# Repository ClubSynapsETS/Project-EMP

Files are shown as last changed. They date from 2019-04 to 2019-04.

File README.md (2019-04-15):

# Project REACH

In the last decade, advences in the domain of electromyography has made it more available to the general public. Which lead to innovation such as a the MYO armband, a commercialised SEMG device. 
These new methods have provoqued a renewed interest in developing more complex prosthetic hands now that more reliable control method to easily control them. Combined with the current trend in biotechnology to solve every problem with machine learning, and you optain the insparation behind project REACH.  

REACH Extends Arm Control for Humans is Myo controlled prothestic arm designed for transradial amputes. It uses a real-time classifier to distinguish between mutually exclusive poses made by human arm by monitoring surface myoelectric (SEMG) generated by muscle contraction on 8 points around the arm. This give us access to 9 distinct commands to control hand with 5 degres of freedom.

## Road Map
### 1) Mechanics
- `/mechanics`        --Contains CAD files and assembling instructions
### 2) Prosthetic Firmware
- `/Firmware`
   - `/Motion_control`     -- Actuator control scheme and modeling of finger mouvement
       - `finger_interce.c`  
       - `finger_interce.h`   
   - `/Pose_classification` --Classifier logic 
       - `pipeline.c`
       - `pipeline.h`
   - `/bluetooth`        -- Bluetooth service connecting to the MYO armband
      - `ble_app.c`
      - `ble_app.h`
      - `myohw.h`             -- Thalmic lab's BLE command and configuration list
   - `/main`             -- top level logic 
      - `app_main.c`
      - `app_main.h`

**Other import files:**
- `/SVM_modle`         -- Instruction on how to remake the model from scratch
   - `/raw_dataset`        -- Raw EMG data file for each pose from the MYO armband
   - `/extraction`         -- Code to extract feature from each data file
   - `Multilabel_linearSVC_MyoSynapsETS.ipynb`   --Traning and testing pipeline using Jupyter

**Parallel Project to be united in the future**
https://github.com/ClubSynapsETS/HandGestureRecongnition

## Getting Started
**Hardware setup** <br>
- `Myo armband` --Thalmic labs has discontinued this products
- `Prosthetic control board`
    - `Solderless Breadboard`
    - `ESP32-DevKitC`
    - `2x 12V Halfbridge (L6202)`
    - `Jumper Wires`
    - `4x PQ12 Cable Adapter`
- `A printed and assembled Prosthetic hand` --

**Connection layout** <br>
#TODO

**Programming the ESP32** <br>
A quick guide on a Linux platform can be followed from here. For a full guide on each operating system follow the official guide of Espressif's website.
https://docs.espressif.com/projects/esp-idf/en/latest/get-started/index.html#step-1-set-up-the-toolchain

Open Terminal, and run the following commands: <dr>

    - mkdir ~/esp
    - cd ~/esp
    - git clone --recursive https://github.com/espressif/esp-idf.git

Setup IDF environment variable <dr>

    - export IDF_PATH=~/esp/esp-idf

Install Python requirements <dr>

    - python -m pip install --user -r $IDF_PATH/requirements.txt

Get the project and program the microcontroller <dr>

    - cd ~/esp
    - git clone https://github.com/Synapse/Project-EMP.git
    - cd Project-EMP
    - make menuconfig
        - Serial flasher config
            - /dev/ttyUSB0
            - exit exit
    - make -j4 flash monitor

**Your REACH grasp** <br>
Place the Myo armband around your forarm following this picture. 
Wait for the connection to be established between the Myo and the ESP32. All Myo armbands have the same hardware address but different IDs, this means that a connection is possible as long as the Myo is on the forarm and charged.
Possible poses
  * Writs flexion
  * Wrist extension
  * Fist
  * Finger Spread

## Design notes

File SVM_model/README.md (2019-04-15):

# SVM Model

If this project was to able to be fully intergrated inside of the prothesis using a 60 MHz microcontroller while managing 5 actuator and receving 1600 bytes a seconds from the myo, a complex algorithm wasn't possible. Thus the linear support vector machine was chosen, for even if it is restrictive in the type of data it can learn from, it's actual classifier is simple dot product operation.

## Requirements
    - Python3
    - Jupyter
   **Installing requirments** <br>
    - pip3 install -r requirements

## Generating experiment data
When it comes to performing the acquisitions, a protocol was established to ensure consistent results.

As mentioned earlier, the acquisition of EMG data was done with the Pewter tool, which in turn depends on the Myo connect software.

##### Placement of the arm band
Band details             |  Band position
:-------------------------:|:-------------------------:
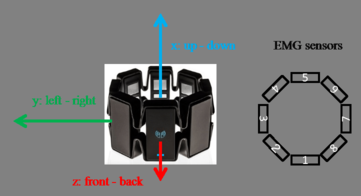
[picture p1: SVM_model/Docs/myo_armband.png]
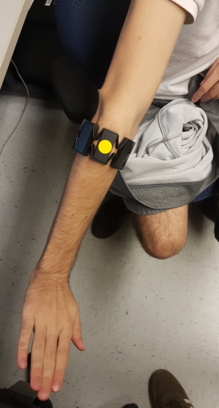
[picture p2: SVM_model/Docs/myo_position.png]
  |  
	
The yellow sticker placed on the Myo (right picture) corresponds to the sensor no.8 (left picture). Also, the USB port on the band should be pointing towards the user's hand.

**Acquisition sequence** <br>
As seen on the "Signal anatomy" figure, the acquisition data is divided into two stages: a resting stage and active stage. This is because we followed a protocol when acquiring training data :

* Place hand in a relaxed position (no strain in the muscles) for about 1 second.
* Place hand in the wanted pose and hold the pose for about 2 seconds.

We chose this approach because it makes it easier to isolate the wanted data during preprocessing and because it ensures consistency throughout the data set.

## Exploring the dataset
We made a jupyter file to explore our dataset.
1. First select the pose dataset to explore
2. Select the index to observe <br>

###### data_observation_script.ipynb
Raw channel                |  RMS equivilent
:-------------------------:|:-------------------------:
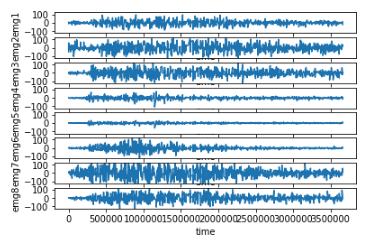
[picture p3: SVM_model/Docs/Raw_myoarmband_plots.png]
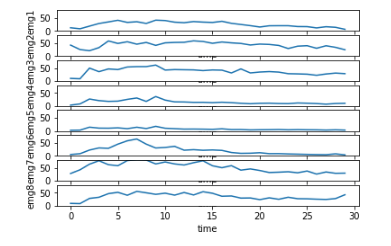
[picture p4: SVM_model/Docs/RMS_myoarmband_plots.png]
 | 

NOTE: RMS representation is the calculation of the root mean square (RMS) of 50 data points on a channel, representing 250 ms of data as a ssingle value. Which outputs a vector of size 8.

By observing each pose, we'll discover that each of them has a different EMG channel that drives the movement. For exemple Wrist_flexion is driven by the muscle under channel 7. The other ones are: Fist & channel 4, Wrist_extension & channel 5, Finger_spread & channel 2.

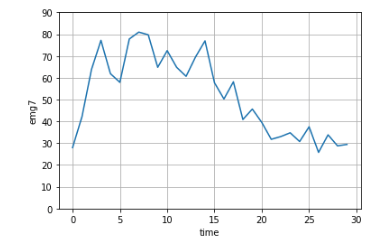
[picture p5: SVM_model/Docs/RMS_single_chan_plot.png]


## Feature Extraction

Now that we've identified some sort of partern in our dataset, we can start extracting features from each experiments. The first step is to split each experiments into matrix of 8x50 in order represent a state in a time interval of 250 ms. But there is a problem in the way we have been gathering data from our experiments. There is, in fact, three distinct states inside of a single experiment. Usually, we would start recording while our hand is in a resting postion then transition into the desired pose. This is represented into the following plot.

 

This means that we also need to label each intervals. We can do that by using the RMS representation of the signal we've identifiedduring the exploration process and setting the threshold at which we can say for certain that the movement has begun. This threshold will depend on many caractheristics, but when passing value of 20 we can say that the arm has stop resting and at 35 the movement we're doing has gegun. Sometimes, the experiment began during the desired pose and there isn't rest nor transition state, the rull still hold true. The only problem occures when the main signal goes back under that set threshold. We can label those as unknow state since we can know for certain what was going on at that precise period of time.

    - `notes_Hand_close.txt`
    - `notes_Hand_open.txt`
    - `notes_Wrist_flexion.txt`
    - `notes_Wrist_extension.txt`

These file contains the note of a script that has gone trough the entire dataset and wrote notes using this format: <br>
             [ file_num, rest_end_index, pose_begin ] [exception_interval]

Using those notes, we can now extract features from the dataset and label them using this script.

##### feature_extract_v1.py

We have now obtain labeled vector each represting a state. Our project's dataset offers 5 classes with a total if just under 12,000 labeled vectors ready for learning algorithm.

##### /full_data_set/pose_instant_data.json <br>
Rest :0             || size = 2139  <br>
Hand close :1       || size = 1959  <br> 
Hand open :2        || size = 2200  <br>
Wrist extension :3  || size = 2522  <br>
Wrist flexion :4    || size = 2457  <br>
None :5             || size = 268 

## SVM

Training the support vector machine algorithm is a simple task using python. Instead, here is the classification report and the confusion for a linear support vector classifier passed trough standard scaler. 

Here is a plot of the cofusion matrix of the function testing our model. <dr>

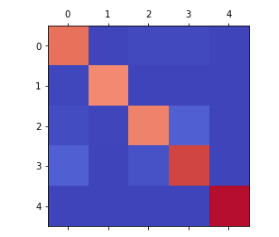
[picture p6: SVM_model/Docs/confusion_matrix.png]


These are statistics success score fo the classifier.
 
              precision    recall  f1-score   support

           0       0.89      0.96      0.93      2139
           1       0.98      0.98      0.98      1959
           2       0.95      0.89      0.92      2200
           3       0.92      0.90      0.91      2522
           4       1.00      1.00      1.00      2457

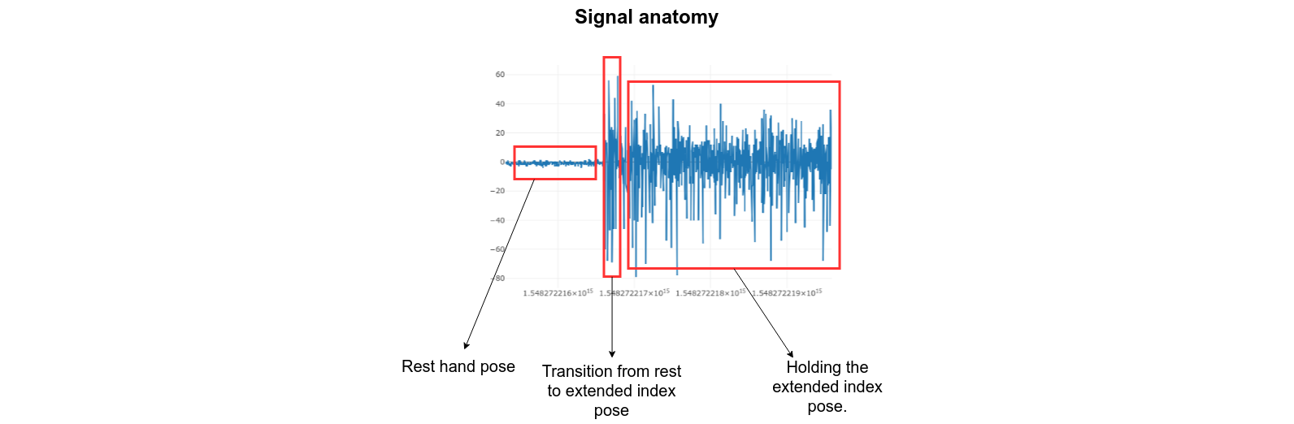
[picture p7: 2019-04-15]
SVM_model/Docs/signal anatomy.png

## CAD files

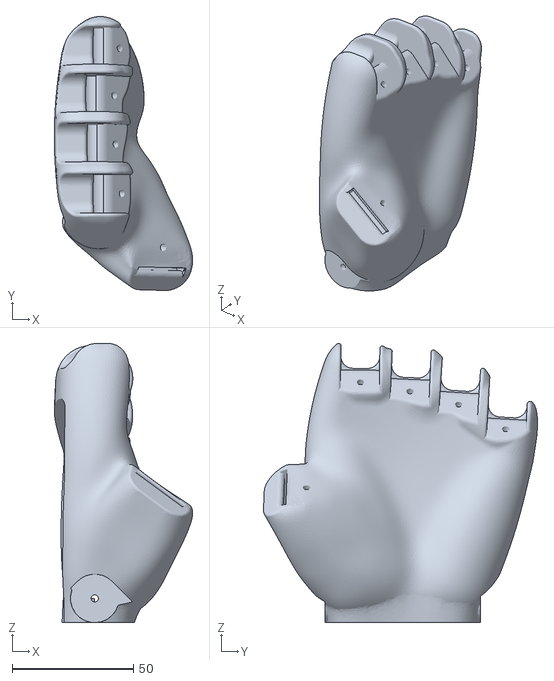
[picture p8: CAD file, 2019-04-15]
Mechanics/FINAL_PROTOTYPE_REACH_LOUIS_SEGUIN/HAND_PALM_MODIFIED.STL
57.0 x 112.9 x 115.1

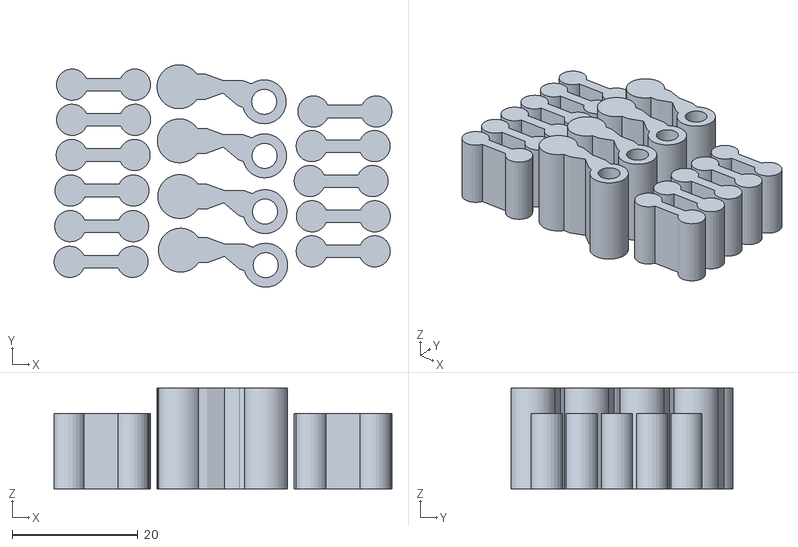
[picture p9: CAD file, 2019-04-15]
Mechanics/FunMove_Finger_Joint.stl
53.8 x 35.4 x 16.0

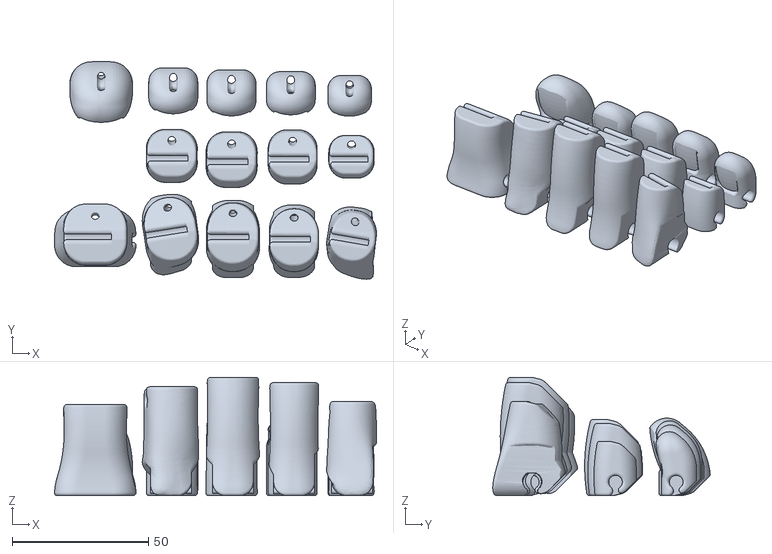
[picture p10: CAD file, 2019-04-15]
Mechanics/FINAL_PROTOTYPE_REACH_LOUIS_SEGUIN/FunMove_LH_Finger.STL
118.3 x 79.9 x 43.5

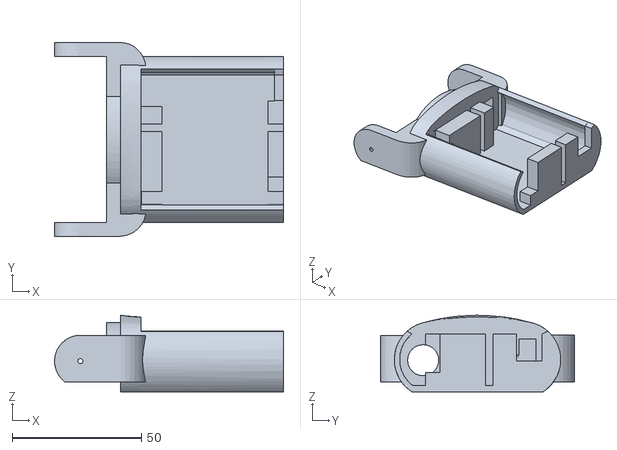
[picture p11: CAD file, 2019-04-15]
Mechanics/FunMove_Motor_housing.stl
88.5 x 74.9 x 29.6

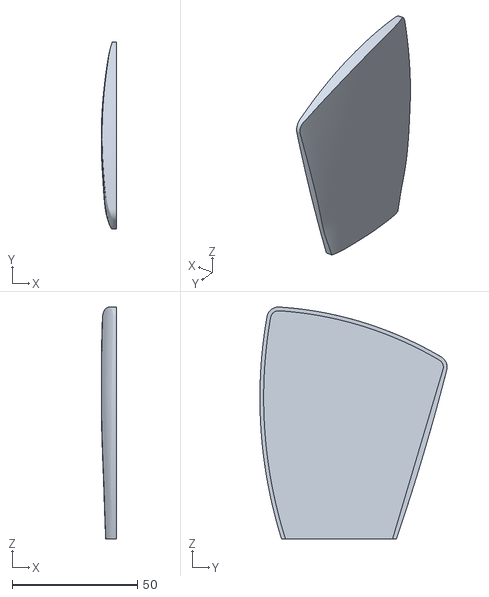
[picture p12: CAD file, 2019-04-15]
Mechanics/FINAL_PROTOTYPE_REACH_LOUIS_SEGUIN/HANDCOVER_MODIFIED.STL
6.16 x 74.6 x 92.5

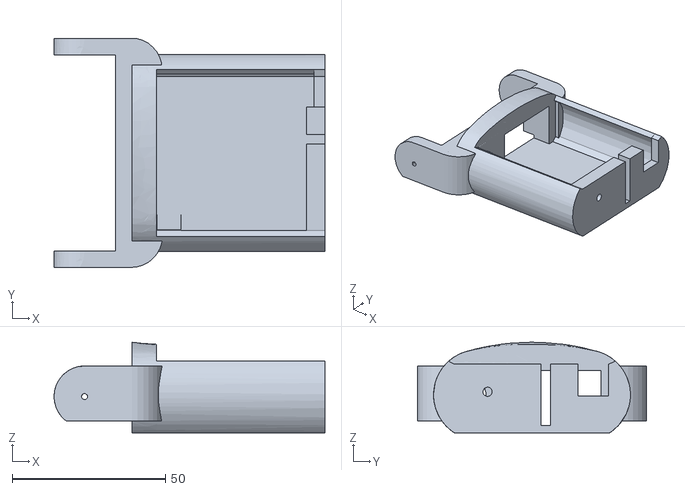
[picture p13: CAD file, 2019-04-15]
Mechanics/FINAL_PROTOTYPE_REACH_LOUIS_SEGUIN/ACTUATOR_HOUSING_MODIFIED.STL
88.5 x 74.9 x 29.6

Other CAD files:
Mechanics/FINAL_PROTOTYPE_REACH_LOUIS_SEGUIN/FunMove_Finger_Joint.STL

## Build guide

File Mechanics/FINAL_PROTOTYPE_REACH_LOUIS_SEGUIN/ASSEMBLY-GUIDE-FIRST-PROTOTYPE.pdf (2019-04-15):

## ASSEMBLY GUIDE FIRST PROTOTYPE-SYNAPSETS

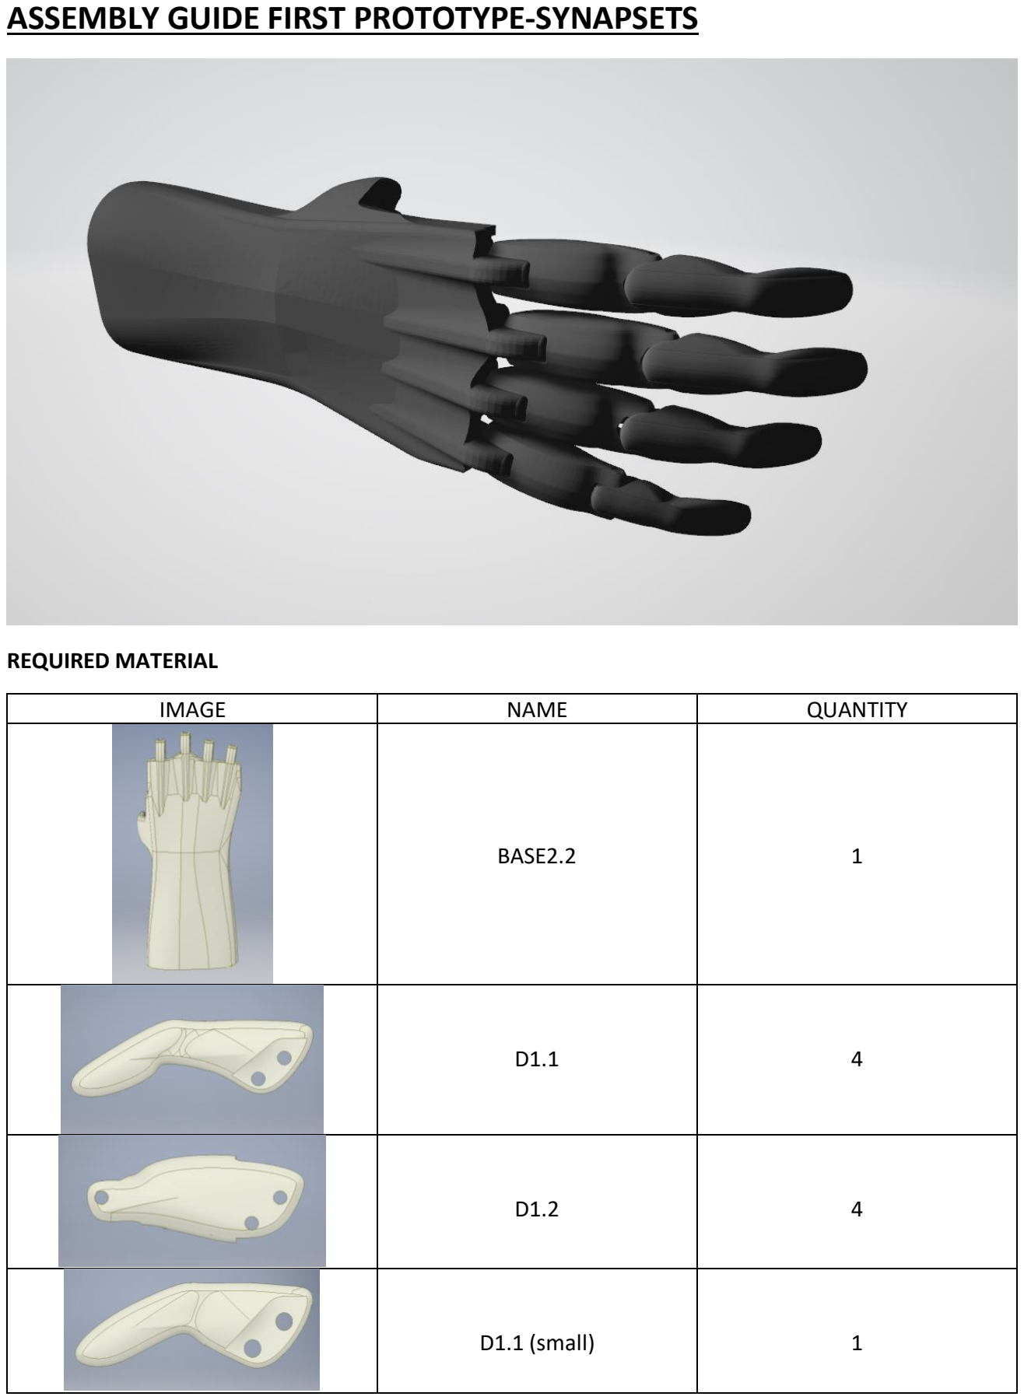
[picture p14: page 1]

REQUIRED MATERIAL

IMAGE | NAME | QUANTITY
| BASE2.2 | 1
| D1.1 | 4
| D1.2 | 4
| D1.1 (small) | 1

| D1.2 (petit) | 1
| PIN (3X16mm) | 12
| PIN (3X 7mm) | 8
| ACTUONIX PQ12 | 4
| YOKE | 4
| M3 SCREW | 8
| M3 NUT | 8
| D1.3 | 3
| D1.3 (petit) | 1

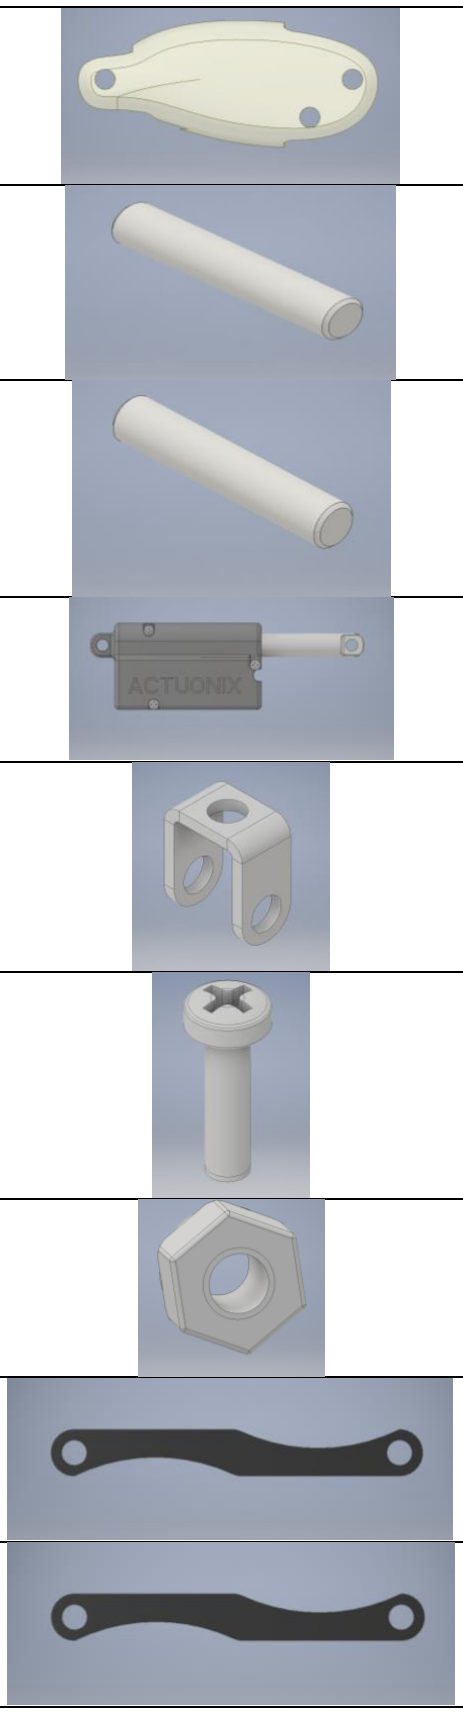
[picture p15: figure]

| | PALM | …
| | THUMB | …

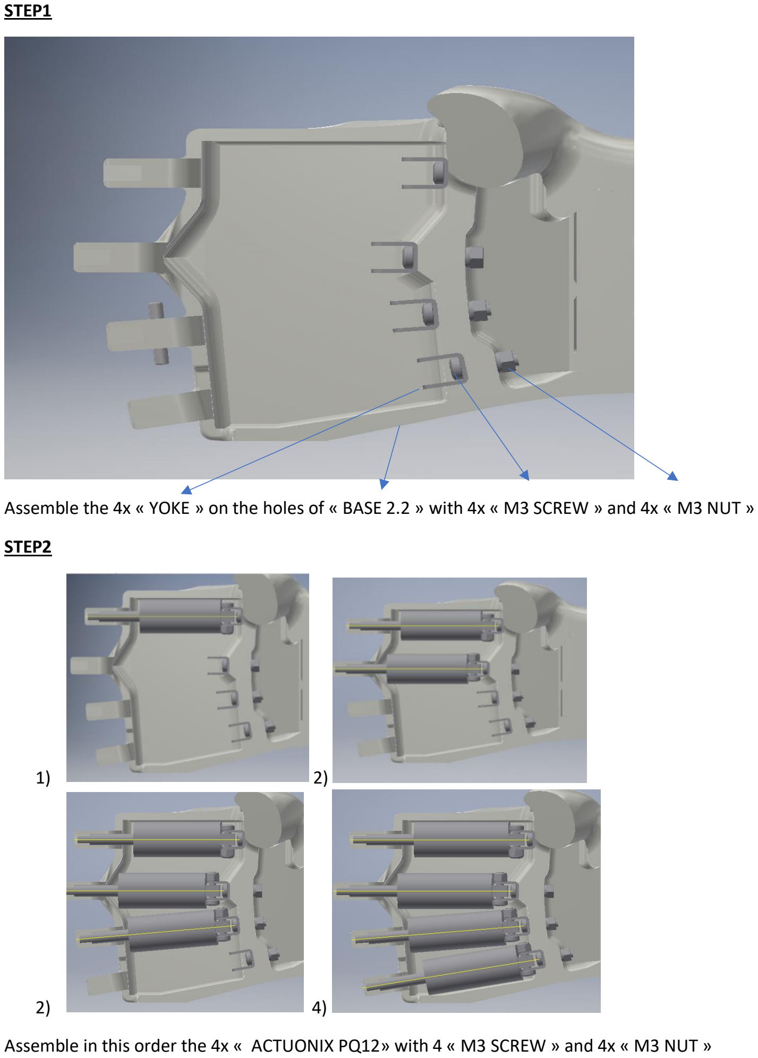
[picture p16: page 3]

STEP1

Assemble the 4x « YOKE » on the holes of « BASE 2.2 » with 4x « M3 SCREW » and 4x « M3 NUT »

STEP2

1) 2)
2) 4)

Assemble in this order the 4x « ACTUONIX PQ12» with 4 « M3 SCREW » and 4x « M3 NUT »

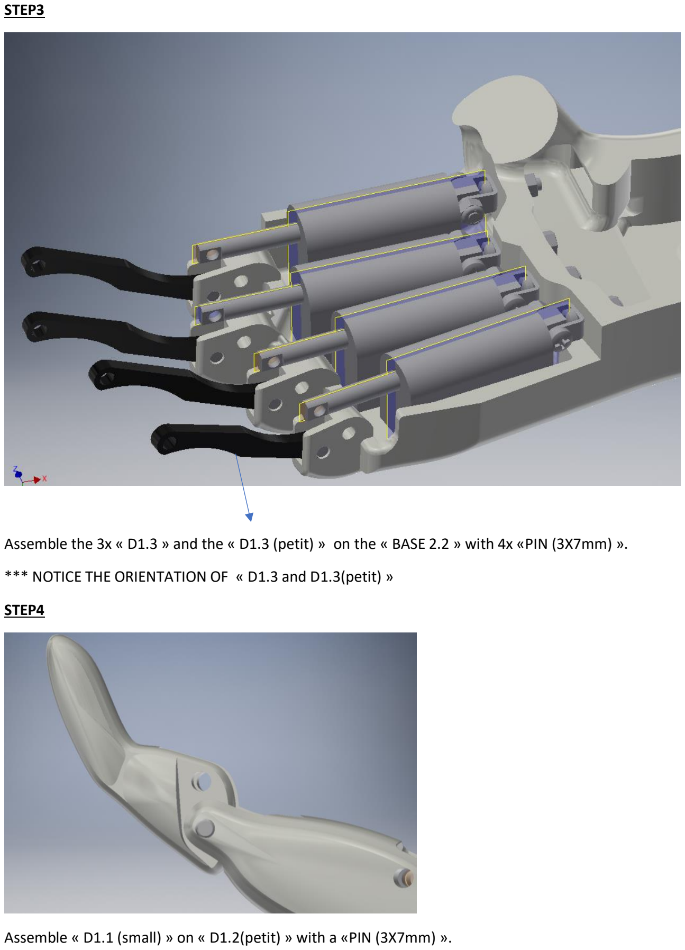
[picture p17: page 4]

STEP3

Assemble the 3x « D1.3 » and the « D1.3 (petit) » on the « BASE 2.2 » with 4x «PIN (3X7mm) ».

*** NOTICE THE ORIENTATION OF « D1.3 and D1.3(petit) »

STEP4

Assemble « D1.1 (small) » on « D1.2(petit) » with a «PIN (3X7mm) ».

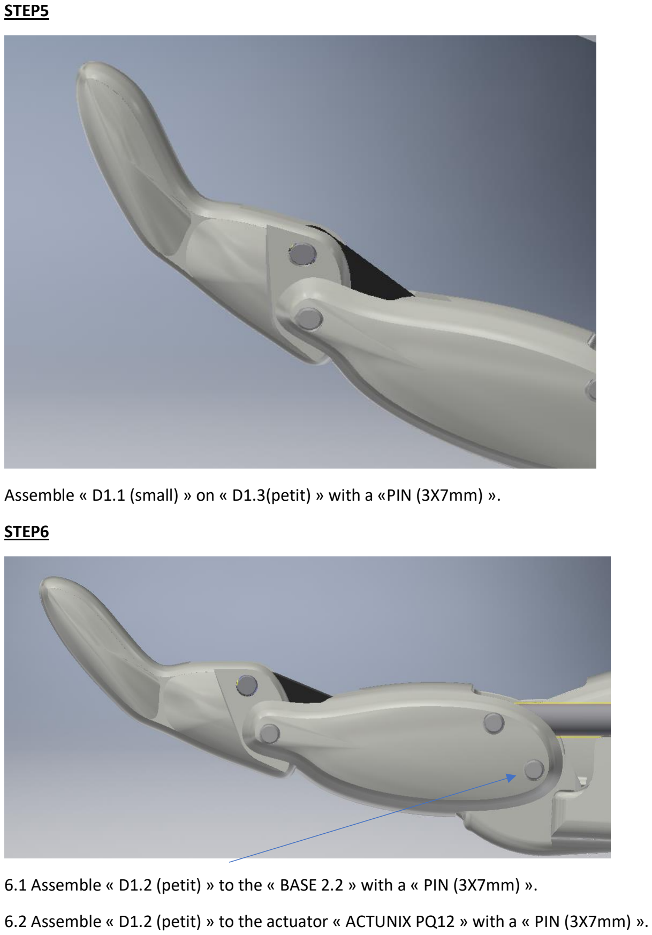
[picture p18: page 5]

STEP5

Assemble « D1.1 (small) » on « D1.3(petit) » with a «PIN (3X7mm) ».

STEP6

6.1 Assemble « D1.2 (petit) » to the « BASE 2.2 » with a « PIN (3X7mm) ».

6.2 Assemble « D1.2 (petit) » to the actuator « ACTUNIX PQ12 » with a « PIN (3X7mm) ».

STEP7

Repeat STEP4 to STEP6 with the other fingers. For the other fingers, « D1.1(small) » becomes « D1.1 » and « D1.2(petit) » becomes « D1.2 ». Assemble the fingers in this order : ring finger, middle finger and index finger.

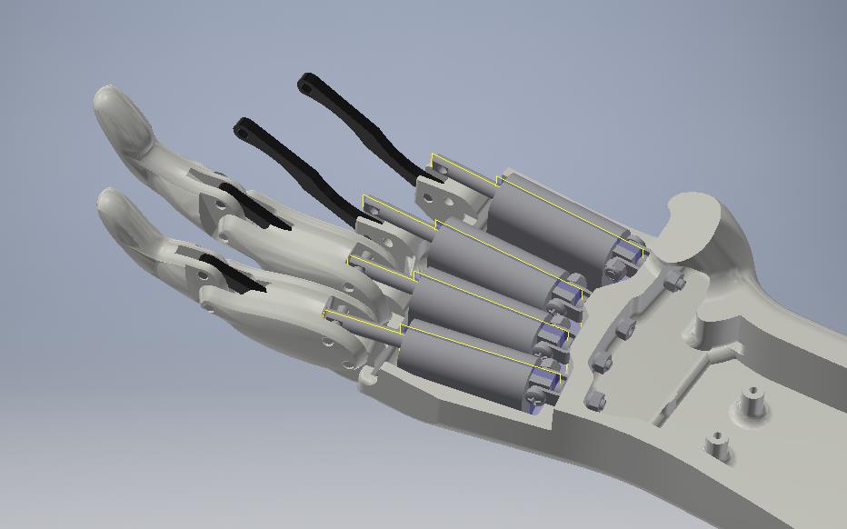
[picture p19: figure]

7.1

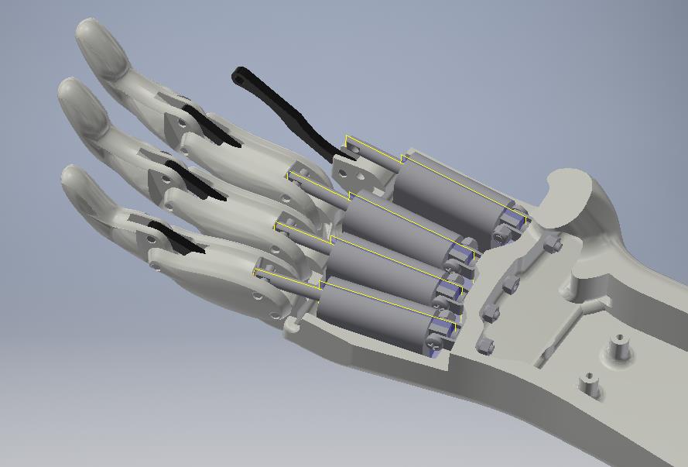
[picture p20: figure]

7.2

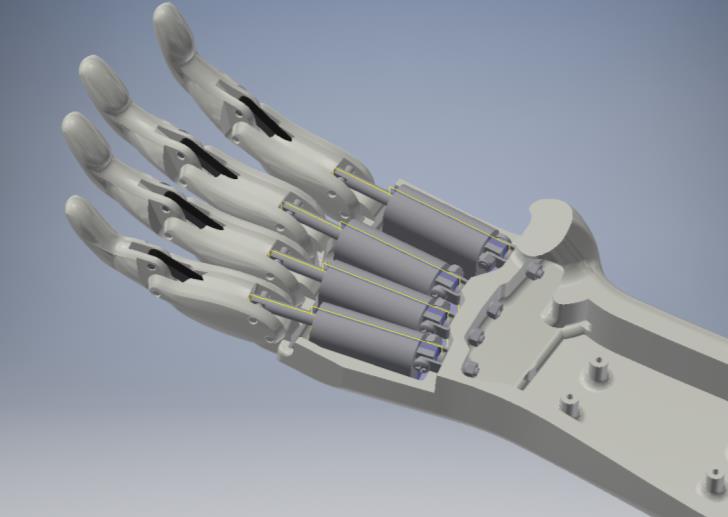
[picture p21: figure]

7.3

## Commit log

2019-04-15 adding pictures
    [FunMove_Finger_Joint.stl, FunMove_LH_Cover_2.stl, FunMove_LH_Finger.stl, FunMove_LH_Handcover.stl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]
2019-04-15 Final push (hopefully)
    [ACTUATOR_HOUSING_MODIFIED.STL, FunMove_Finger_Joint.STL, FunMove_LH_Finger.STL, HANDCOVER_MODIFIED.STL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]
